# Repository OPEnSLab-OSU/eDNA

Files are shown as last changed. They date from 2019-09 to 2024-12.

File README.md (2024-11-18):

# eDNA Sampler | [Updates](https://github.com/OPEnSLab-OSU/OPEnS-Lab-Home/wiki/eDNA-updates) | [Senior Design Updates](https://github.com/OPEnSLab-OSU/OPEnS-Lab-Home/wiki/eDNA-Senior-Design-Updates) | [Github](https://github.com/OPEnSLab-OSU/eDNA) | [ednaUI](https://github.com/OPEnSLab-OSU/ednaUI) | [ednaServer](https://github.com/OPEnSLab-OSU/ednaServer)

Current Project Team:

Lead: **Marc Belinga** 

Mechanical: **Hendy Kurniawan**

Software:**Marc Belinga** 

Electrical: **Reece Fitch**

## Overview

Organisms leave traces of DNA as they move through their environments. The extraction of these DNA traces is known as environmental DNA (eDNA). eDNA provides scientists and researchers with a non-invasive and sensitive way to detect and quantify species. However, traditional eDNA sampling consists of manually filtering water, which is labor and cost-intensive for remote locations. Furthermore, commercialized solutions are expensive and require a field operator. This eDNA sampler project aims to provide an affordable, open-sourced, remotely deployable, fully automated, and customizable alternative. 

## Description

The eDNA Sampler can run up to 24 inline filter units with support for different conditions including pressure, time, and volume limit. The pumps can deliver a maximum of 350mL/min of flow with each solenoid valve separating the filter housings to minimize cross-contamination. At the end of each sample, the desired stabilizing solution can be injected to fully submerge the filter for long-term storage. An optional river depth sensor can provide a proxy for flow to correct eDNA concentrations to allow for improved quantification of organisms. Data acquired during operation including water depth, pressure, temperature, and flow rate will be stored on a microSD card as a CSV file, which allows easier data export and analysis. A web application is specially designed for the eDNA Sampler for in-field programming, real-time sensor updates, scheduling tasks, and manual operations. The full sampler is estimated to be ~$6000 each.

<p align="center">
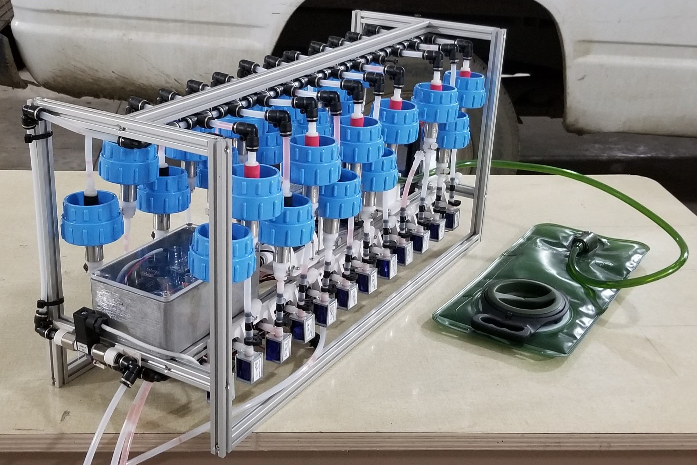
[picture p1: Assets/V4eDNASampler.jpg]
  
</p>

## Field Updates
The eDNA sampler was successfully deployed in Alaska, where it operated under varying levels of turbidity and successfully collected DNA across all conditions. Over the course of six days, the sampler consistently performed three sample collections per day at multiple locations, showcasing its reliability in diverse environments. The battery capacity proved sufficient for multiple days of operation without requiring a recharge, enabling extended fieldwork in remote areas. Additionally, the sampler achieved an average margin of error of 9% in measuring water volume, demonstrating robust performance while highlighting areas for further refinement.

## Objectives

Determining the level of cross-contamination between filters during sampling.
Testing alternatives to ethanol, such as Longmire's solution, for safer and more convenient preservation during field deployments.
Improving the accuracy of water volume measurements using a tipping bucket mechanism.

| Main Control Board     |
|:-------------:|
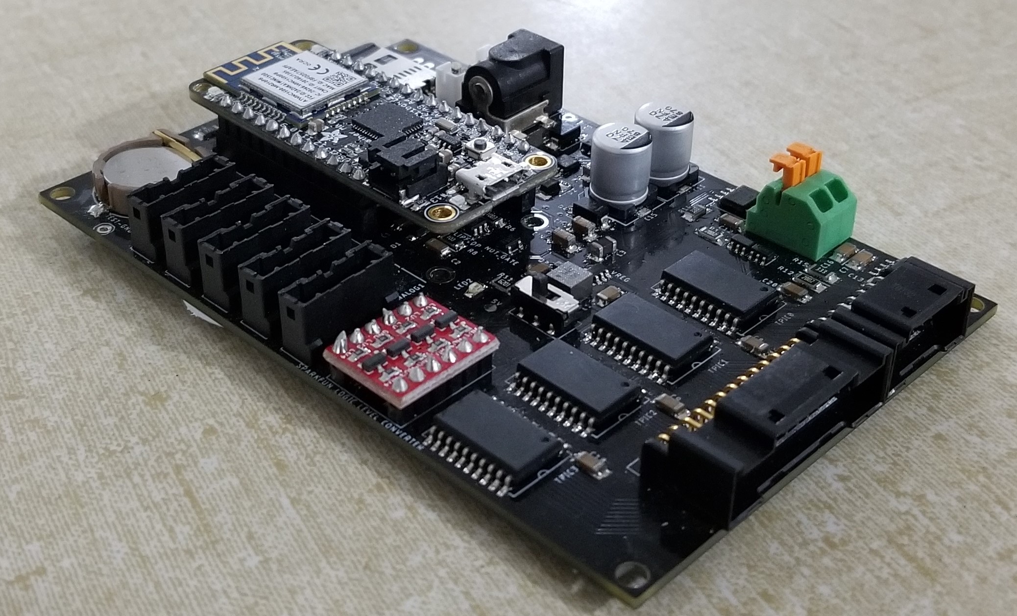
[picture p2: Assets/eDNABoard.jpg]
|      | 

| Browser Application     |
|:-------------:|
|  |

## Future

Finalizing tests for Longmire’s solution to replace ethanol as the preservative.
Implementing a tipping bucket mechanism to improve measurement accuracy.

## Resource List

*  [A Build Guide for the current version (V4) of the eDNA Sampler](https://www.overleaf.com/read/rsvcsjwgfrgj) (Work in Progress)
*  [How to update an assembly in Fusion360](https://www.youtube.com/watch?v=EKoYnxrryUQ)

<!---*  [eDNA GitHub](https://github.com/OPEnSLab-OSU/eDNA)

## [eDNA Updates](https://github.com/OPEnSLab-OSU/OPEnS-Lab-Home/wiki/eDNA-updates) | [Github](https://github.com/OPEnSLab-OSU/eDNA) -->

## Problems & Solutions

Identified logistical challenges with ethanol preservation during field deployment, prompting the exploration of Longmire's solution as an alternative.
While we did average a 9% error in water volume measurements plans are currently being put in place to integrate a tipping bucket to further improve accuracy.
Continued troubleshooting to address filter clogging issues.

Feel free to contact the lab/developer if you have other ideas to solve, improve, or upgrade the eDNA sampler.

Marc Belinga: belingam@oregonstate.edu

## Keywords
eDNA, genomic, sampling, sampler, sample, environmental DNA

## Former Team Members:
Electrical: **Bao Nguyen**, **Sean Booth**,**Jacob Field**, **Kai Roy**

Programming: **Kawin Pechetratanapanit**, **Emannuel Moncada** 

Mechanical: **Torrey Menne**, **Aaron S Arvidson**, **Nikhil Wandhekar**, **Ethan Pohlschneider**, **Tilford Li**, **Danil Kryuchkov**, **Dylan Heisey**, **Joshua Iler**

## Reference
* [Types of Hydraulic Pumps](https://www.youtube.com/watch?v=Qy1iV6EzNHg)

* [eDNA AGU 2019 Poster](https://github.com/OPEnSLab-OSU/OPEnS-Hypnos/files/3996793/eDNA.poster_jsspptx.2.pdf) | [ESSOAR](https://www.essoar.org/doi/abs/10.1002/essoar.10501740.1) | 10.1002/essoar.10501740.1

*  [Inline Pressure Sensor](https://github.com/OPEnSLab-OSU/OPEnS-Lab-Home/wiki/Inline-Pressure-Sensor) (Outdated)

*  [Inline Flow Sensor](https://github.com/OPEnSLab-OSU/OPEnS-Lab-Home/wiki/IDT-Inline-Flow-Sensor) (Outdated)

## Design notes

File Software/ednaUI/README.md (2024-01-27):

# ednaUI 🚀

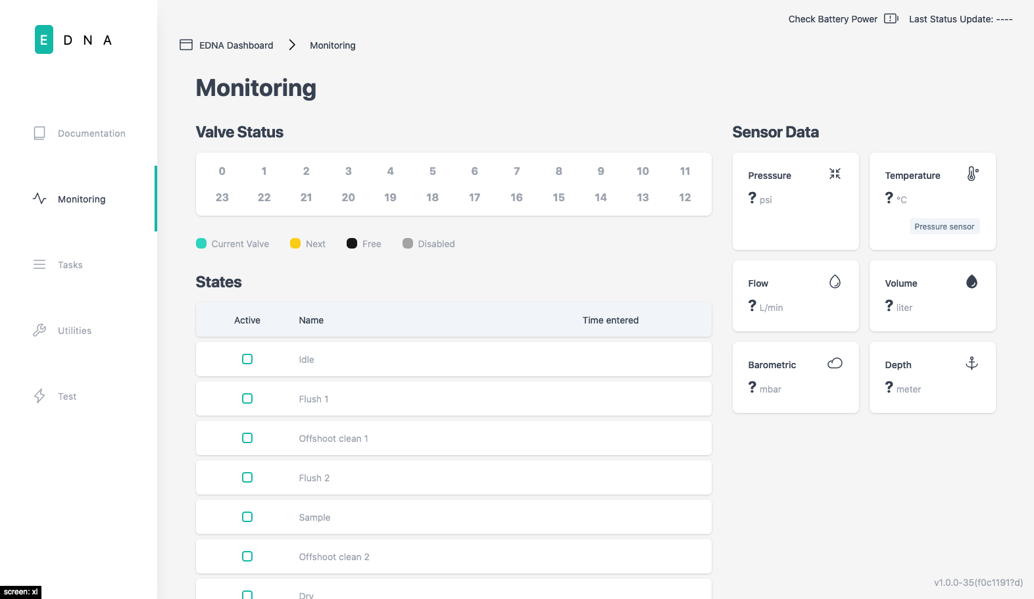
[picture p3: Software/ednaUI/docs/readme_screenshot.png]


### Contributors
- [Kawin Pechetratanapanit](https://github.com/kawinie)
- [Nathan Jesudason](https://github.com/NathanJesudason)

### Top Level Index
- [1 About](#1-about)
- [2 Components](#2-components)
- [3 React Redux Store](#3-react-redux-store)

## 1 About

ednaUI is a browser-based application intended to be used as the primary way for controlling the [ednaServer](https://github.com/OPEnSLab-OSU/eDNA-Server) backend. Uses React, Redux Toolkit, Tailwind CSS, and Webpack.

- Real-time status monitoring of sensor data and states
- Task configuration and management
- Utility functions

## 2 Components
- [2.1 Monitoring](#21-monitoring)
    - [2.1.1 SensorTile](#211-sensortile)
    - [2.1.2 StateTable](#212-statetable)
    - [2.1.3 ValveStatus](#213-valvestatus)
- [2.2 NotFound](#22-notfound)
- [2.3 TaskConfig](#23-taskconfig)
    - [2.3.1 ConfigCard](#231-configcard)
    - [2.3.2 ConfigListItem](#232-configlistitem)
    - [2.3.3 SubmitCard](#233-submitcard)
    - [2.3.4 TaskForm](#234-taskform)
- [2.4 Tasks](#24-tasks)
   - [2.4.1 NewTaskInput](#241-newtaskinput)
   - [2.4.2 TaskTile](#242-tasktile)
- [2.5 Test](#25-test)
- [2.6 Utilities](#26-utilities)

### 2.1 Monitoring
These components are associated with the monitoring tab, giving you information about the current state of the sampler.

#### 2.1.1 SensorTile
The component that holds sensor readings.
#### 2.1.2 StateTable
The component that holds current state information
#### 2.1.3 ValveStatus
The component that keeps track of which valve is available, about to be used, being used, or already used.

### 2.2 NotFound
This is the 404 Page

### 2.3 TaskConfig
These components are associated with the task configuration page, which appear when editting a task.

#### 2.3.1 ConfigCard
This component is used by the TaskForm inside TaskConfig.
#### 2.3.2 ConfigListItem
This component contains a button that takes the user to the top of a page.
#### 2.3.3 SubmitCard
This component handles saving, deleting, scheduling, and unscheduling tasks.
#### 2.3.4 TaskForm
This component holds the values for the various parameters of a task.

### 2.4 Tasks
These components are associated with the tasks tab

#### 2.4.1 NewTaskInput
This component handles entering in a new task name
#### 2.4.2 TaskTile
This component visualizes each of the tasks on the task tab

### 2.5 Test
This is a tab only available in development mode that allows the user to test out a few features.
### 2.6 Utilities
This tab provides all of the utility functions, such as hyperflush and rtc update.

## 3 React Redux Store
- [3.1 Actions](#31-actions)
    - [3.1.1 getStatusUpdate](#311-getstatusupdate)
    - [3.1.2 getTaskCollection](#312-gettaskcollection)
    - [3.1.3 createTask](#313-createtask)
    - [3.1.4 getTask](#314-gettask)
    - [3.1.5 updateTask](#315-updatetask)
    - [3.1.6 deleteTask](#316-deletetask)
    - [3.1.7 scheduleTask](#317-scheduletask)
    - [3.1.8 unscheduleTask](#318-unscheduletask)
    - [3.1.9 setLoadingScreen](#319-setloadingscreen)
- [3.2 models](#32-models)
    - [3.2.1 TaskServerSchema](#321-taskserverschema)
    - [3.2.2 StatusServerSchema](#322-statusserverschema)
- [3.3 reducers](#33-reducers)
    - [3.3.1 status](#331-status)
    - [3.3.2 initialTaskCollection](#332-initialtaskcollection)
    - [3.3.3 taskCollection](#333-taskcollection)
    - [3.3.4 loadingScreen](#334-loadingscreen)

### 3.1 Actions
An action describes what to do with new data after an event.

#### 3.1.1 getStatusUpdate
gets information from the sampler such as valves, currentState, utc, pressure...
#### 3.1.2 getTaskCollection
Gets all tasks from the sampler
#### 3.1.3 createTask
Requests to the sampler to make a new task with a provided name
#### 3.1.4 getTask
Gets a particular task based on its ID
#### 3.1.5 updateTask
Sends updated task information to server
#### 3.1.6 deleteTask
Deletes a task based on its ID
#### 3.1.7 scheduleTask
Schedules a saved task, sending its ID to the sampler
#### 3.1.8 unscheduleTask
Unschedules a task based on its ID
#### 3.1.9 setLoadingScreen
Stores whether the loading screen should be shown or not.

### 3.2 Models
Defines objects to store data in

#### 3.2.1 TaskServerSchema
Defines a task object, and a dictionary of tasks is used to store all tasks
#### 3.2.2 StatusServerSchema
Defines a status object.

### 3.3 Reducers
Reducers take new information and update the state

#### 3.3.1 status
Updates status
#### 3.3.2 initialTaskCollection
Used only in develop, creates an initial list of tasks of random IDs
#### 3.3.3 taskCollection
Updates taskCollection
#### 3.3.4 loadingScreen
Updates whether the loadingScreen should be displayed or not.

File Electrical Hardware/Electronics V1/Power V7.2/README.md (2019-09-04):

# 12V Version 7.2
Power Control Board for microcontroller projects, designed at OPEnS Lab OSU.

The board use a [D-Flipflop](https://www.digikey.com/product-detail/en/texas-instruments/SN74LVC1G175DBVR/296-17617-1-ND/706599) to store the current state of the system.

| D-Flipflop     |
|:-------------:|
|  |

| Schematic Name | Pin Name                  |
|----------------|---------------------------|
| `Q`            | Input - tied HIGH         |
| `D`            | Output to power regulator |
| `CLK`          | Clock                     |
| `!CLR`         | Clear - Reset             |

The flipflop IC is work based on raising, positive edge of the clock (posedge)
The input `D` is always tied HIGH.
The `CLK` is normally pulled low until triggered by the Feather.

> In the original sleep state:
 * `D` is HIGH
 * `Q` is HIGH
 * `CLK` is LOW
 * `CLR` is HIGH

> when the RTC fires the alarm:

`CLR` (reset) is pulled down to GND -> make the output `Q` LOW
		-> Turn on the power regulator. The state remain the same since there is no change in the clock
		
> When Feather fired the shutdown signal:

`CLK` (reset) goes low->high which copy the input `D` to the output `Q`. Since `D` is always high,
		the output `Q` will change to HIGH -> shutdown the voltage regulator

System stay as sleep until the RTC fires again -> reset the flipflop

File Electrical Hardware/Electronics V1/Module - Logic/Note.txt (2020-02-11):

BAO NGUYEN - OPENSLAB

4/24/2019
Disconnect MOSI pin from the board for wifi usesage.
Pin A5, now is connect dirrectly to the main PCB for Shift Register Data
-	A5 --> SHIFTDATA
-	MOSI(M0) is not connected to anything
-	D13 -> HB_IN2 deleted
-	D12 -> HB_IN1 deleted
-	D6 -> HB_IN2 (connect to H-bridge)
-	D5 -> HB_IN1 (connect to H-bridge)

-	D13 -> Button3
-	D12 -> Button2
-	D9  -> Button1

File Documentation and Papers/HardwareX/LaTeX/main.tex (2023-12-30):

% GENERAL INFORMATION: HardwareX is an open access journal established to promote free and open source designing, building and customizing of scientific infrastructure (hardware). For more details on best practices for sharing open hardware see http://www.oshwa.org/sharing-best-practices/

\documentclass[11pt, letterpaper]{article}
\usepackage[utf8]{inputenc}
\usepackage[margin=1.5cm]{geometry} % Default 1.5cm, For review 2cm?
\usepackage{titlesec}
\usepackage{tabu}
\usepackage{enumitem}
\usepackage{amssymb}
\usepackage{xcolor}
\usepackage{verbatim}
\usepackage{graphicx}
\usepackage{setspace}
\usepackage{lineno}
\newlist{selectlist}{itemize}{2}
\setlist[selectlist]{label=$\square$,leftmargin=*,noitemsep,topsep=0pt}

\usepackage{lmodern}

\usepackage{hyperref}
\hypersetup{
    colorlinks=true,
    linkcolor=blue,
    filecolor=magenta,      
    urlcolor=blue,
}
 
\urlstyle{same}

% Set up the section label formatting
\titleformat{\section}[block]{\hspace{1em}\bfseries}{\thesection.}{0.5em}{} 
\titleformat{\subsection}[block]{\hspace{1em}}{\thesubsection}{0.5em}{}

% Settings for Review
%\doublespacing
%\linenumbers

\begin{document}
% Create the title block
\begin{flushleft}

% Remove all text in italics when filling out the template and replace with your manuscripts corresponding text in regular font.
%\textit{Text in italics are template instructions. Remove and replace all instructions with regular font text.}

\setlength{\parindent}{0pt}
\setlength{\parskip}{10pt}
% \textbf{\large HardwareX article template}

%
% Background Information
%
%Insert title
%Max. 20 words. A good title should contain the fewest possible words that adequately describe the content of a paper.
\textbf{Title} \\
PolyWAG: Autonomous filtered water sampling for eDNA 
%\textit{Please avoid acronyms and abbreviations where possible.}

%Insert Authors
\textbf{Authors} \\
Kai Roy * Riley Prince * Marc Belinga * John Selker * Chet Udell
% List all authors. Please mark the corresponding author with (*)

%Insert Affiliations
\textbf{Affiliations} \\ 
(Insert Affiliations)
%\textit{Please include the full address of each author institution}

%Insert Contact Email
%Include institutional email address of the corresponding author
\textbf{Corresponding author’s email address and Twitter handle}\\ 
\textit{Institutional email address preferred. If you have a Twitter handle, please add it here ‘twitter: \@....’}

%Insert Abstract
%Max. 200 words. Remember that the abstract is what readers see first in electronic abstracting and indexing services. This is the advertisement of your article. Make it interesting, and easy to be understood. Be accurate and specific, keep it as brief as possible.
\textbf{Abstract} \\ 
Environmental DNA, eDNA, is an ideal way of researching aquatic environments to determine what species are present in an area the biodiversity of an area, and if any invasive or endangered species are present . Traditional sampling of environmental DNA (eDNA) consists of manually filtering water,  which is labor and cost-intensive for remote locations. Furthermore, commercialized solutions  are either expensive or require a field operator to function.  We have built an eDNA capable of autonomous multi-sampling for a greatly reduced price compared to existing technologies. Our PolyWAG eDNA sampler system is a water sampling device that collects DNA samples via 47mm filter and provides a non-invasive, safe and autonomous means of eDNA collection. The sampler can hold 24 filters and is designed to be easily replaced and reusable. A browser application is used for real-time monitoring, scheduling tasks, and data logging for time, pressure, flow, and filtered volume. Additionally, the sampler design is openly published, modular and is constantly being tested to help us optimize our software and hardware to give us the best results. The 9-step  sampling sequence helps reduce cross contamination significantly. Our machine can be deployed for an extended period. It is completely autonomous and costs around \$6000.

%\textit{Max. 200 words. Remember that the abstract is what readers see first in electronic abstracting \& indexing services - make it brief, specific, interesting and easy to understand. If a research article refers to your hardware, cite that research article here.}

%Insert Keywords
% At least 3 keywords. There is no limit on the no. of keywords you can list. Please remember that effective keywords should not repeat words appearing in your title, and should be neither too general nor too narrow.
\textbf{Keywords}\\
Environmental DNA * Sampling * Arduino * Data Logging \\
%\textit{Add at least 3 keywords and a maximum of 6 keywords.}

%
% Specification Table
%
\newpage
\textbf{Specifications table}\\
% \textit{Please replace the italicizied instructions in the right column of the table with the relevant information about your hardware.}
\vskip 0.2cm
\tabulinesep=1ex
\begin{tabu} to \linewidth {|X|X[3,l]|}
	\hline  
	\textbf{Hardware name} & 
	\textit{PolyWAG}
  	\\
  	\hline 
  	\textbf{Subject area} & 
  	\textit{Environmental, planetary and agricultural sciences}
  	\\
  	\hline 
  	\textbf{Hardware type} & 
  	\textit{Field measurements and sensors}
  	\\ 
	\hline 
	\textbf{Closest commercial analog} &
  	\textit{Dartmouth Ocean Technologies' eDNA Sampler}
  	\\
	\hline \textbf{Open source license} &
  	{CERN Open Hardware License \newline 
  		GNU General Public License v3.0}
  	\\
	\hline \textbf{Cost of hardware} &
  	\textit{\$3800 (Cost of just components)\newline
  		\$6000 (Cost with labor included)}
  	\\
	\hline \textbf{Source file repository} & 
  	% Link to the source file repository
    % insert a DOI URL to an approved source file repository:  Mendeley Data, theOSF, or Zenodo (instructions).  For example: "https://doi.org/10.5281/zenodo.3346799"
    % If there is no external repository write “Available in the article”
  	\textit{If you’ve uploaded your source files to an approved repository (\href{http://osf.io}{\underline{OSF}}, \href{https://data.mendeley.com/}{\underline{Mendeley Data}} or \href{https://zenodo.org/}{\underline{Zenodo}}) write the DOI URL here. For exemple:  \href{http://doi.org/10.17605/OSF.IO/WGK7Q}{http://doi.org/10.17605/OSF.IO/WGK7Q}}  
	% DOI URL to an approved source file repository: \href{https://data.mendeley.com/}{Mendeley Data}, the \href{http://osf.io}{OSF}, or \href{https://zenodo.org/}{Zenodo} \href{https://doi.org/10.5281/zenodo.3346799}{(instructions)}. \linebreak For example: "https://doi.org/10.5281/zenodo.3346799" \linebreak If there is no external repository write “Available in the article"}
  	\\

%\hline \textbf{OSHWA certification UID} \vskip 0.1cm {\it (OPTIONAL)}&
  %Insert OSHWA Certification UID (optional)
%{\it We encourage you to apply for a free \href{https://certification.oshwa.org/}%{\underline{OSHWA Certification}}, which confirms your work is open-source compliant.
%\vskip 0.2cm
%If certification has been acquired, insert the OSHWA UID here. For example: “CH000005”. In your OSHWA certification project description, include a link to your HardwareX publication and the tag \#HX.
%\vskip 0.2cm
%If you haven’t acquired certification, please delete this row of the specifications table.}

\\\hline
\end{tabu}
\end{flushleft}

% create the main body of the paper

\newpage
\section{Hardware in context}

% Include a short description of the hardware, putting into context of similar open hardware and proprietary equipment in the field.
%\textit{Write a short description of the hardware and provide context, i.e., describe similar open hardware and proprietary equipment in the field.}
Environmental DNA (eDNA) is DNA derived from mucus, feces, gametes, and carcasses \cite{web:USGS:eDNA}. Many things can be learned once this DNA is put through sequencing. eDNA can be used to determine what species are present in an area, the biodiversity of an area, and if any invasive or endangered species are present \cite{web:NOAA:eDNA}. eDNA sampling provides scientists and researchers a non-invasive, rapid, cost-effective and sensitive way to detect and quantify species in many environments.  
\newline\par
Traditional sampling of environmental DNA consists of manually filtering water, often requiring one or more researchers to be on location for days or weeks \cite{}. The filtration process varies depending on the researcher, but it is common to pull a sample of water with a bottle and pour that water into a funnel containing a filter. This can be connected to a vacuum pump to expedite the filtering process. After the sampling process is completed, the filters need to be preserved and the setup cleaned to avoid cross contamination \cite{}. This process is labor intensive, cost intensive, and can be dangerous, especially for remote locations. While commercialized solutions to this problem exist, they either still require an operator to be on location or are very expensive. Smithroot’s commercial solution offers a simplified process with additional data collection such as GPS location for a fair price, around \$8,000 \cite{web:smithroot}. A disadvantage of this solution is that it is not fully autonomous, still requiring an operator to be on location to use the device \cite{web:smithroot}. An alternative is the DOT Sampler which is a fully autonomous solution that is capable of multiple samples (20+ samples) and is also submersible but comes at a cost of ~\$55,000 \cite{art:DOT}. 
\newline\par
The solution designed by the OPEnS Lab is the middle ground of these two solutions. While it is not submersible (limiting its potential sampling environments), it is capable of autonomous, multi-sample operations for extended periods of time (approximately one month) for the cost of \$6,000. The two core priorities for our design are its autonomous function and the cross-contamination. The autonomous function of the  sampler is important for a handful of reasons. An autonomous system requires less researcher hours spent in the field. This has cost benefits from the reduced hours worked and safety benefits when sampling in hazardous environments.     

\section{Hardware description}
% Describe the hardware, highlighting the customization rather than the steps of the procedure. Highlight how it differs/which advantage it offers over pre-existing methods. For example, how could this hardware: be compared to other hardware in terms of cost or ease of use, be used in the development of further designs in a particular area, and so on.

% > Add 3-5 bulleted points to broadly explain to other researchers how the hardware could be potentially useful to them, for either standard or novel laboratory tasks, inside or outside of the original user community.

%	\textit{Describe your hardware, highlighting the customization rather than the steps involved in the procedure. Explain how it differs from other hardware and the advantages it offers over pre-existing methods. For example, how does this hardware compare to other hardware in terms of cost or ease of use, or how can it be used to develop further designs in a particular area? 
%	\vskip 0.3cm \noindent
%	Add 3-5 bullet points which broadly explain to other researchers - inside or outside of the original user community - how the hardware could help them, with either standard or novel laboratory tasks.}

The eDNA sampler we have developed is an autonomous multi-sampling device that collects eDNA samples from water via 47mm filter holders and provides a non-invasive, safe, and autonomous means of DNA collection. The sampler can hold 24 of these filter housing and are designed to be easily replaced and reusable. The sampler is controlled by a custom logic board with an Adafruit M0 Feather Wi-Fi microcontroller loaded with a webserver to act as the interface for the sampler’s operations. This webserver hosts a browser application which is used for real-time monitoring, scheduling tasks, and data logging for time, pressure, temperature, flow, and sample volume. This data is located stored onto an SD Card for later data analysis. 

\begin{center}
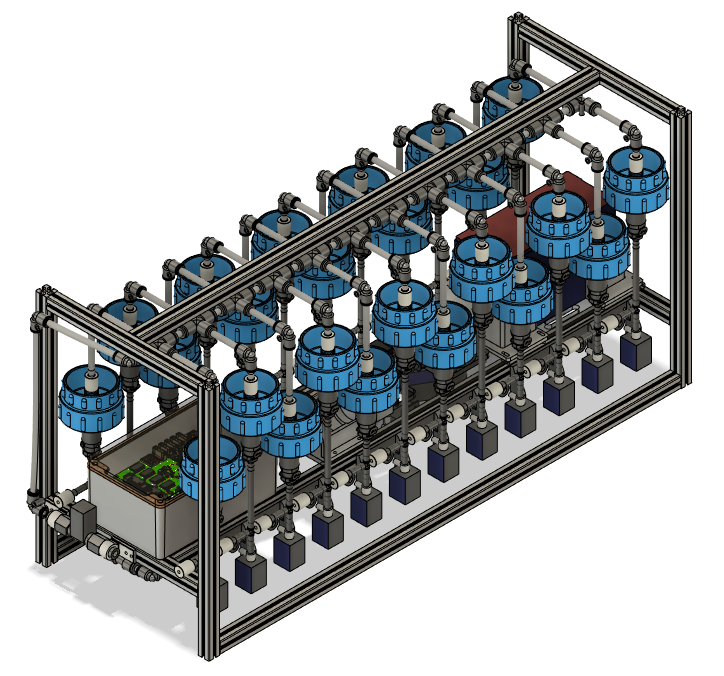
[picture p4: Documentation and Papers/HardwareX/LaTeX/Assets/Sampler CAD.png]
	 %Replace with actualy image?
\end{center}

\subsection{Hydraulics}
The hydraulics of the sampler can be roughly split into the following sections:
\begin{itemize}
	\item The Pump and Inputs
	\item The Lower Hydraulics
	\item The Filters
	\item The Upper Hydraulics and Outputs
\end{itemize}
There are three inputs into the sampler: one for air, one for preservative, and one for water. The preservative input is connected to a hydration bladder where the preservative of choice can be stored. The water input has a prefilter at the front end of the tube to prevent debris from entering the sampler. Three valves are used to control the flow from these inputs with the air preservative being regulated by a solenoid valve and the water being controlled by a ball valve. These three valves connect into a single tube connected to the input of the peristaltic pump.
The pump is capable of 400ml/min of flow under ideal conditions. The output of the pump connects directly into the Lower Hydraulic Rail. 

\begin{center}
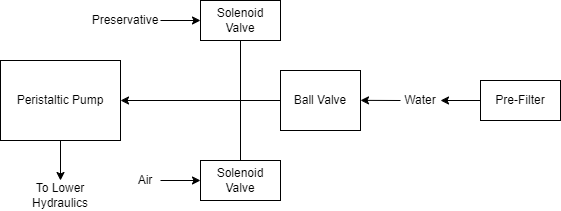
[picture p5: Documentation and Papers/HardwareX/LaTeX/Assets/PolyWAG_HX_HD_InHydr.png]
	
\end{center}

The Lower Hydraulic Rail consists of 24 solenoid valves connected parallel to each other which controls which filter liquid flows through. The valves are split into two sets, one on each side of the sampler. In between these two sets is a M32JM-000105-100PG pressure and temperature sensors. The temperature is logged for later use and the pressure is used for monitoring, stopping an operation if the pressure exceeds a certain margin. At the end of the Lower Hydraulic Rail is another solenoid valve which allows for the lower hydraulics to be purged of their current contents when necessary.

\begin{center}
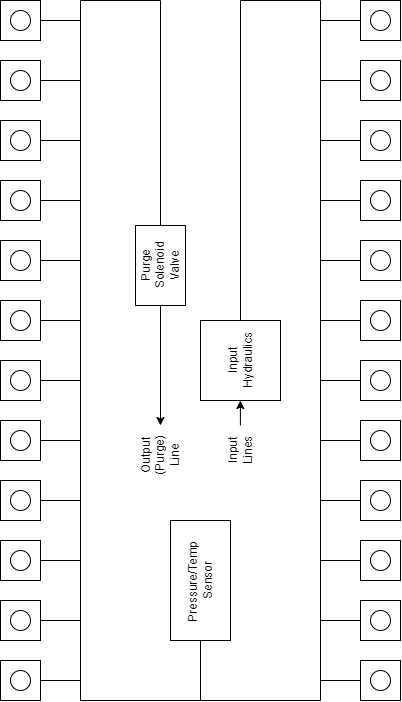
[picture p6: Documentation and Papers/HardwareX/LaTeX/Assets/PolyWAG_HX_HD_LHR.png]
	
\end{center}

After the solenoid valve there is a tee connection that goes to a one-way check valve and a modified Advantec filter. The one-way check valve allows air into the solenoid valve that opens when the pump runs backwards. The Advantec filter is modified with a CPC quick disconnect and a one-way check valve. The one-way check valve is connected to the Upper Hydraulics and is used to prevent liquid from going backwards through the filter. The Upper Hydraulics simply connects the output of all the filters to one central line that goes through a flow meter and out of the sampler. 

\begin{center}
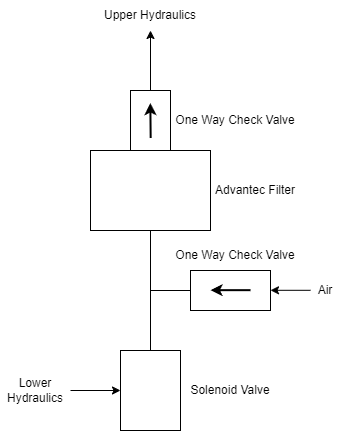
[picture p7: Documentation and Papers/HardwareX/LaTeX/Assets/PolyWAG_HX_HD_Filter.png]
	
\end{center}

\subsection{Sampling Procedure}
Having worked on multiple iterations of the sampler, we have decided to go with a 13-step sampling sequence that helps reduce cross contamination significantly. This sequence can be split into 9 unique steps: Idle, Prefilter Clear, Flush, Offshoot Clean, De-pressure, Sample, Preservative Flush, Preservative, Air Flush, and End.

\begin{center}
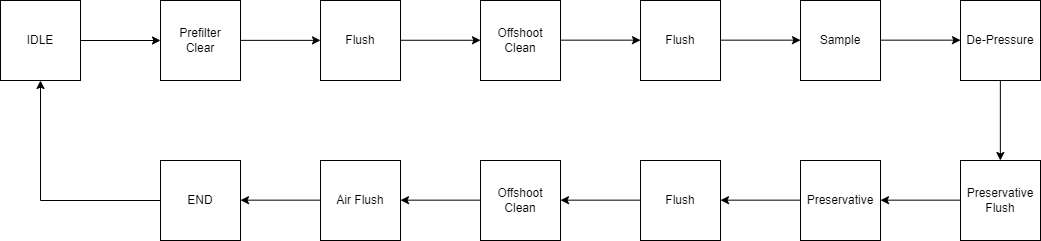
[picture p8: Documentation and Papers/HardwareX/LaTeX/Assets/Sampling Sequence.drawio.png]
	
\end{center}

The Idle state is the default state of the sampler. This is where the sampler waits for a signal from the RTC to move to the first/next state of the Sampling Sequence. If the sampler is not in sleep mode, this is when a client would interact with the UI to do a handful of tasks such as setting up a Sampling Schedule or using the other task utilities. If the sampler is in sleep mode, then only the RTC and supporting circuits are powered. This means there is no way to interact with the sampler without exiting sleep mode.
\newline\par
Once the RTC sends the signal to start a sample procedure, the sampler enters the Prefilter Clear (PC) state. In this state, the purge and input ball valve are opened, and the pump is run in the backwards direction. This will allow for air to flow from the purge and out the input line. This is used to clear the prefilter of anything that might be clogging it, such as accumulated debris. This state runs for X seconds, before moving onto the next state. 
\newline\par
The Flush state and the proceeding Offshoot Clean (OC) state are used to prepare the lower hydraulics before the Sample state. The Flush state starts with the purge valve and the ball valving opening, then the motor starts to run in the forward direction. This fills the lower hydraulics with sample liquid and clears out/dilutes and liquid that remained from previous sample. The Flush state runs for the time specified when the Sampling Schedule is created. We recommend a Flush time of 6 minutes. 
\newline\par
The OC state closes the purge valve and opens the filter valve (for the filter which is about to be used. The pump runs backwards for a few seconds. This clears anything that might be in the tube between the valve and the filter (what we refer to as the offshoot). The Flush state is run one more time before moving to the Sample state.
\newline\par
Like the name suggests, the Sample state is where the system pushes the sample water through the filter. This is done by opening the Filter and Ball Valve and running the pump in the forward direction. The system moves to the next state when the target Sample Volume is reached. This volume is measured by a Flow Meter on the filter output line. Ideally, the state is terminated when the target volume is reached. There is an additional condition that will end the Sample state and that is the Sample Time. This time cutoff was added since the filter clogs and the flow rate decrease rapidly during the sample process. To prevent the sample state running for too long, the time limit was implemented. Both conditions are set during task scheduling. Since the pressure greatly increases due to the clogged filter, the de-pressure state is used to reduce the pressure in the lower hydraulics to ensure that the valves can operate consistently.
\newline\par
The Preservative Flush (PF) and Preservative (P) states are the next states in the sequence after the de-pressure state. The PF state is nearly identical to the Flush state except the Preservative input valve is used instead of the ball valve. The goal of this state is to saturate the lower hydraulics with preservative, preventing additional sample water that may have been stored in the lower hydraulics from going through the filter. If this water was allowed through the filter, then the Sample Volume would be inaccurate by the end of the sequence. The P state is like the Sample state except preservative is the input fluid instead of sample water. This state runs for a time specified by the user during scheduling.  
\newline\par
After the P state, another Flush and OC state runs to purge the leftover preservative in the lower hydraulics. After these two states, an Air Flush (AF) state is run which is identical to the Flush and PF states but uses the air valve as the input instead of the other two inputs. This ensures that any liquid that is in the lower hydraulics is purged. 
\newline\par
After the AF state occurs, the system sets an RTC alarm for the time of the next sample. The system then moves into Idle and if the system was in sleep mode, then the system will go into its low power state.

\subsection{Utilities}

\begin{center}
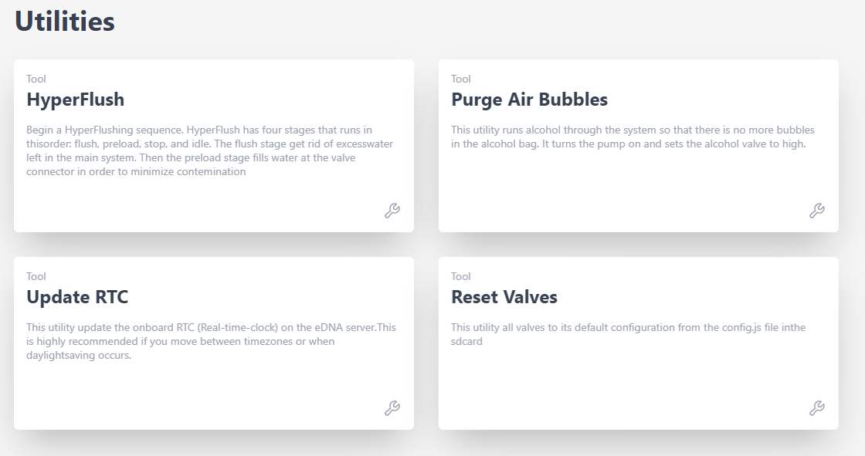
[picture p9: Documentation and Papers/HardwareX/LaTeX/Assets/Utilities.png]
	
\end{center}

The HyperFlush utility runs water through every filter sequentially for a few seconds per filter. This is mainly used for cleaning out the system after a sample task (i.e., a set of 24 samples) to prevent any unwanted cross contamination. This utility can also be used to test the basic functionality of the sampler, as nearly every component is activated during this sequence. 
\newline\par
The Preservative Air Purge (PAP) utility turns the pump on and opens the alcohol valve for 10 seconds. This runs some alcohol through the system and removes air bubbles from the alcohol bag. Often it helps to use this utility multiple times and to tilt the Preservative Bladder so that the air is near the port.
\newline\par
The Update RTC utility is needed to make sure that the time on the sampler matches your local time, so scheduling a task will remain accurate. Whenever the system is fully depowered (ie the battery is removed), or when new code is uploaded to the microcontroller, the RTC will need to be updated. It is also recommended that the RTC is updated when there is a daylight-saving change, or when you move between time zones.
\newline\par
The Reset Valves Utility is used when valves have been sampled that you want to be sampled again. This is required since the system ‘locks’ the filter valves when they have been used in a sample, this prevents samples from being corrupted accidentally. The code does not let you sample a valve multiple times without being reset to prevent messing up a sample. It is important to note that this utility will reset all valves, not a specific one.

\subsection{Electronics}
\begin{center}
	
\end{center}

The PolyWAG Sampler is designed with a custom electronics control board that can be split into 8-10 blocks with an Adafruit Feather M0 at its core. These blocks consist of the microcontroller/Wifi Block, Power, RTC, and sleep control blocks, and the output blocks consisting of the Shift Register, Pump, and Ball-Valve H-Bridge Blocks. 

\begin{center}
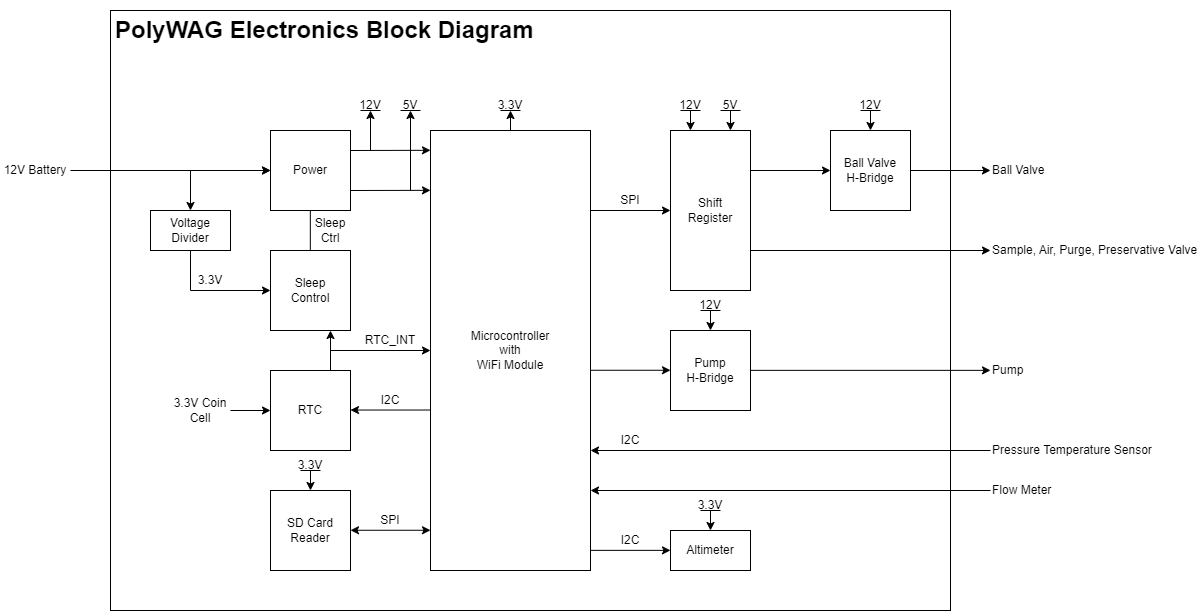
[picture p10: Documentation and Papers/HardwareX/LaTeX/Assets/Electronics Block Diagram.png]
	
\end{center}

The power block consists of a reverse polarity current (RPC) circuit and a voltage regulator circuit. The RPC Circuit was added to protect the 12V battery from current flowing backwards through the system. While the battery has its own protection circuits, they lock the battery in the case of a short and need to be reset using the battery charger. The RPC circuit was added to prevent any “permanent” power loss while in the field. The voltage regulator circuit is a 12V to 5V regulator with an enable pin that connects to the sleep control circuit. This is used to save power during long term deployments. 
\newline\par
The RTC and sleep control circuit are used to keep track of time and to save power respectively. The sleep control circuit controls the output of the power circuit and is constantly being power by a simple voltage divider circuit. It is basically a Flip Flop circuit that is reset when the RTC triggers an interrupt. The RTC circuit is used to keep track of the time between samples and is powered by a coin cell while power is off. This allows it to keep accurate track of time and signals an interrupt when its internal alarm is triggered. This interrupt is used to both turn power back on and to inform the microcontroller that it is time for a sample. If noise causes the sleep control circuit to reactivate power, the microcontroller will see that the RTC did not trigger the interrupt and will fall back into power saving mode. 
\newline\par
The shift register circuit consists of 4 8-bit shift registers connect to the microcontroller via SPI. The shift registers are pull-down style shift registers where the ‘output’ pins are pulled to ground. This allows the shift registers to control devices that use higher logic voltages. This allows us to control the 27 12V solenoid valves with a 5V IC. The shift registers are also used to control the H-bridge for the Ball valve. The H-bridge for the pump is controlled directly by the microcontroller itself. 
\newline\par
The board contains an SD Card circuit for datalogging purposes. The data is logged every second and includes the current state, time, and data from the sensors. The sensors include an in-line pressure temperature sensors for monitoring the lower hydraulic line and a flow meter out the output for measuring volume.
\newline\par
The microcontroller of choice is an Adafruit Feather M0 WiFi. The WiFi version of the Feather M0 was chosen as the user interface requires the feather to host a webserver. 

\subsection{User Interface}

\begin{center}
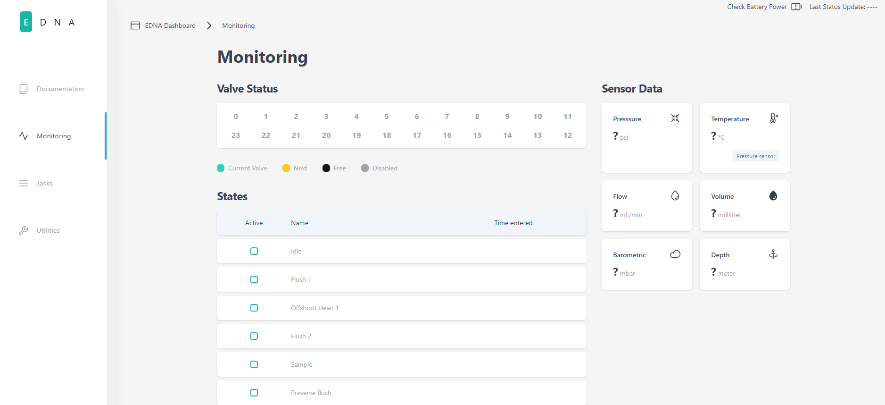
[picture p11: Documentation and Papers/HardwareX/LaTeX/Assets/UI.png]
	
\end{center}

PolyWAG Sampler hosts a webserver that can be connected to via a browser. This acts as the user interface for the system. There are three main sections that make up the user interface: monitoring, tasks, and utilities. The monitoring page displays the data from the sensors, the current state of the sampling procedure, and information on the sampling valves such as the current valve being sampled, and which valves are locked and unlocked. The utilities page is used to activate the utilities mentioned earlier. The tasks page is where sampling tasks are created. Multiple tasks can be created, and each task is saved in memory for later modification and use. This page is also where tasks can be scheduled for sampling. Each task contains the information on which valves are being used as well as for how long each state occurs. 

\subsection{Task Configuration}

\section*{\textit{Design files}}
% The  complete  design  files  must  be  either  uploaded  to  an  approved  online  repository,  uploaded  at the  time  of  submission  on  the  online  Editorial  Manager  submission  interface  as  supplementary materials [CAD files, videos,. . . ], or included in the body of the manuscript [e.g.  figures].  The three approved  online  repositories  are  Mendeley  Data,  the  Open  Science  Framework,  and  Zenodo. See repository instructions: https://doi.org/10.5281/zenodo.3346799

% Design files should be in preferred format for making modifications. See OSHWA’s open-source definition for details: https://www.oshwa.org/definition/

\textit{Your design files should be editable - see \href{https://www.oshwa.org/definition/}{OSHWA’s open source definition of ‘Documentation’} for further details. You must then either:}
\begin{itemize}
\item[$\bullet$]{\it Upload your design files to one of the three approved online repositories - \href{https://data.mendeley.com/}{Mendeley Data} (\href{https://doi.org/10.5281/zenodo.3346799}{instructions}), the \href{https://osf.io/}{Open Science Framework} (\href{https://osf.io/wgk7q/wiki/home/}{instructions}) or \href{https://zenodo.org/}{Zenodo} (\href{https://doi.org/10.5281/zenodo.3346799}{instructions}). We recommend this option as the repositories support versioning of files.}
\item[$\bullet$]{\it Upload your design files as supplementary materials (e.g., CAD files, videos…) to Hardware X’s online editorial system when you submit your manuscript.}
\item[$\bullet$]{\it Include your design files in the body of the manuscript (e.g., as figures).}
\end{itemize}

%
%\textit{The complete design files must be either uploaded to an approved online repository, uploaded at the time of submission on the online \href{https://editorialmanager.com/ohx/}{Editorial Manager} submission interface as supplementary materials [CAD files, videos,\dots], or included in the body of the manuscript [e.g. figures]. The three approved online repositories are \href{https://data.mendeley.com/}{Mendeley Data}, the \href{http://osf.io}{Open Science Framework}, and \href{https://zenodo.org/}{Zenodo}. See repository instructions \href{https://doi.org/10.5281/zenodo.3346799}{here}. Design files should be in preferred format for making modifications. See \href{https://www.oshwa.org/definition/}{OSHWA’s open-source definition} for details.}
%\begin{itemize}
\vskip 0.1 cm
\noindent
\textit{\underline{CAD files:} You are encouraged to use free and open source software packages for creating the files. For CAD files, \href{http://www.openscad.org/}{OpenSCAD}, \href{http://www.freecadweb.org/}{FreeCAD}, or \href{https://www.blender.org/}{Blender} are encouraged, but, if these are not available, we accept source files from proprietary CAD packages, such as Autocad or Solidworks, and other drawing packages.} 
\vskip 0.1 cm
\noindent
\textit{\underline{3D printing:} Supplementary files that facilitate digital replication of the devices are encouraged;  for example, STL files for 3D printing components. We recommend uploading CAD files to the \href{http://3dprint.nih.gov/}{\underline{NIH 3D Print Exchange}} as Custom Labware and then entering the link here.} 
\vskip 0.1 cm
\noindent
\textit{\underline{Electronics:} PCB layouts and other electronics design files can be uploaded to the \href{http://www.ohwr.org/}{\underline{Open Hardware Repository}} or other repositories or as supplementary materials.} 
\vskip 0.1 cm
\noindent
\textit{\underline{Software and firmware:} All software files used in the design and operation of the hardware should be included in the repository. Provide a description of the software and firmware and use extensive comments in the code.}

\section{Design files summary}
\textit{Complete a separate row for each design file associated with your hardware (including the primary design files). Any empty rows should be deleted.}
% Please include a summary of all design files for your hardware by filling rows of the table below
\vskip 0.1cm
\tabulinesep=1ex
\begin{tabu} to \linewidth {|X|X|X[1.5,1]|X[1.5,1]|} 
\hline
\textbf{Design filename} & \textbf{File type} & \textbf{Open source license} & \textbf{Location of the file} \\\hline
%Insert design files
\textit{For example: Design file 1} & \textit{e.g. CAD file, figures, videos} & \textit{All designs must be submitted under an open hardware license. Enter the corresponding open source license for the file.} & \textit{Either enter the URL for the repository or the sentence: "Available with the article".}  \\\hline
\dots & \dots & \dots & \dots \\\hline
\dots & \dots & \dots & \dots \\\hline
% Design file 3 & File type & License & Link \\\hline
\end{tabu}

% For each design file listed in the summary above, include a short description of the file below (one or two sentences)
\vskip 0.3cm
\noindent
\textit{For each design file listed in the summary table above, include a short description of the file below (just one or two sentences per design file).}

\section*{\textit{Bill of materials}}
% For a complex Bill of Materials, the complete Bill of Materials (editable spreadsheet file e.g., ODS file type or PDF file) can be uploaded in an open access online location such as the Open Science Framework repository. Include the link here. Alternatively, the Bill of Materials can be uploaded at the time of submission on the online Elsevier submission interface as supplementary material.

% > To make it easy to tell which item in the Bill of Materials corresponds to which component in your design file(s), use matching designators in both places, or otherwise explain the correspondence.

% > For material type, select from: Metal, semi-conductor, ceramic, polymer, biomaterial, organic, inorganic, composite, nanomaterial, semiconductor, non-specific, or other 

% > \href{https://osf.io/}{\underline{Open Science Framework}} 
Given the number of materials required to build a PolyWAG Sampler, The BOM will be located in an external file and can be found \href{https://docs.google.com/spreadsheets/d/1WZbGYL1k3ne1a8Z1YOA0necr3MgxMj_BiEK7JuaGnzE/edit#gid=1118434588}{\underline{here}}
% Change the link for one that points to Zenodo
% > Add the BOM to Zenodo

\section{Build instructions}
%Provide detailed, step by step instructions for the construction of the reported hardware include all necessary information for reproducing the submitted hardware.
% > Explain and, when possible, characterize design decisions. Including design alternatives if they exist. 
% > Use visual instructions such as schematics, images, and videos. 
% > Clearly reference design files and component parts described in the Design File Summary and Bill of Materials. 
% > Highlight potential safety concerns that may arise

Given the complexity of the PolyWAG Sampler, a Build Instructions section of sufficient detail would be near a hundred pages long. This is why an external build guide document will be linked for those who are interested in knowing how one of these samplers are assembled. This file can be located \href{https://drive.google.com/file/d/1QSpYj-N6-jE-VbXLVelzRzzdIF1lMkuC/view?usp=sharing}{\underline{here}}
% Change the link for one that points to Zenodo
% > Add the Build Guide to Zenodo

\section{Operation instructions}
%Provide detailed instructions for the safe and proper operation of the hardware. 
%> Step-by-step operational instructions for operating the hardware. 
%> Use visual instructions as necessary. 
%> Highlight potential safety hazards.

%%% Kai's Notes
%%% Use Mark's section here
%%% Maybe add a section for physically using the sampler. 

\section{Validation and characterization}
%Demonstrate the operation of the hardware and characterize its performance over relevant critical metrics
%> Demonstrate the use of the hardware for a relevant use case. 
%> If possible, characterize performance of the hardware over operational parameters. 
%> Create a bulleted list that describes the capabilities (and limitations) of the hardware. For example consider descriptions of load, operation time, spin speed, coefficient of variation, accuracy, precision and etc. 

%%% Kai's Notes
%%% Insert Riley's Section once edits are made. 

\section*{}
\noindent
\textbf{Ethics statements}\\

\noindent
The work does not use any human or animal subjects.\\

\noindent
\textbf{CRediT author statement}\\
% CRediT is in initiative that enables authors to share an accurate and detailed description of their diverse contributions to a published work.
% Example:
% Zhang San: Conceptualization, Methodology, Software. Priya Singh: Data curation, Writing- Original draft preparation. Wang Wu: Visualization, Investigation. Jan Jansen: Supervision. Ajay Kumar: Software, Validation. Sun Qi: Writing- Reviewing and Editing.
% Please add a CRediT author statement for your data article here, using the \href{https://www.elsevier.com/authors/journal-authors/policies-and-ethics/credit-author-statement}{categories listed on this webpage}.

\noindent
\textbf{Kai Roy}: Project administration, Hardware(Electrical), Validation, Writing- Original draft \\
\noindent
\textbf{Riley Prince}: Project administration, Methodology, Validation, Data curation, Writing- Original draft \\
\noindent
\textbf{Marc Belinga}: Software, Investigation, Writing- Original draft \\
\noindent
\textbf{Torrey Menne}: Conceptualization, Hardware\\
\noindent
\textbf{Bao Nguyen}: Project administration, Conceptualization, Hardware(Electrical)\\
\noindent
\textbf{Nikhil Wandhekar}: Project administration, Hardware\\
\noindent
\textbf{Nathan Jesudason}: Software, Validation \\
\noindent
\textbf{Kawin Pechetratanapanit}: Conceptualization, Software \\
\noindent
\textbf{John Selker}: Funding acquisition, Supervision \\
\noindent
\textbf{Chet Udell}: Funding acquisition, Supervision \\
\noindent
\textbf{Cara Walter}: Funding acquisition, Supervision, Resources \\

\noindent
\textbf{Auther}: Contribution. \\

\noindent
\textbf{Acknowledgements}\\
% [List here those individuals who provided help during the research (e.g., providing language help, writing assistance or proof reading the article, etc.).] Please also identify who provided financial support for the conduct of the research and/or preparation of the article and to briefly describe the role of the sponsor(s), if any, in study design; in the collection, analysis and interpretation of data; in the writing of the report; and in the decision to submit the article for publication. If the funding source(s) had no such involvement then this should be stated.}

\noindent
\textit{All contributors who do not meet the criteria for authorship should be listed in an acknowledgments section.} 
\vskip 0.2cm
\noindent
\textit{In addition, please list any funding sources in this section. List funding sources in this standard way to facilitate compliance to funder's requirements:}
\vskip 0.2cm
\noindent
\textit{Funding: This work was supported by the National Institutes of Health [grant numbers xxxx, yyyy]; the Bill \& Melinda Gates Foundation, Seattle, WA [grant number zzzz]; and the United States Institutes of Peace [grant number aaaa].}
\vskip 0.2cm
\noindent
\textit{It is not necessary to include detailed descriptions on the program or type of grants and awards. When funding is from a block grant or other resources available to a university, college, or other research institution, submit the name of the institute or organization that provided the funding.}
\vskip 0.2cm
\noindent
\textit{If no funding has been provided for the research, please include the following sentence:}
\vskip 0.2cm
\noindent
\textit{This research did not receive any specific grant from funding agencies in the public, commercial, or not-for-profit sectors.
}\\

%
% References
%
%> Include at least one reference, to the original publication of the hardware you customized.
%> Include other references as required. Include references to put your device in context in the literature. For more information on the reference format in HardwareX please see the Guide for Authors at: https://www.elsevier.com/journals/hardwarex/2468-0672/guide-for-authors
\bibliography{refs}
\bibliographystyle{IEEEtran}

\end{document}

%> Author manuscript checklist
%> ●	HardwareX is a journal dedicated to the exhaustive and fully open source communication of advances in scientific infrastructure. Upon submission the author declares that all information necessary to reproduce the subject of the submission (e.g. bill of materials, build instructions, calibration procedures, source files, code, and safety considerations) is communicated in full and is accessible for use under an open source license. 
%> ●	Is the subject of the submission under an open source license? Are design files in the preferred format for making modifications? As defined by the Open Source Hardware definition. 
%> ●	Can the hardware be reproduced with the details provided in the submission?
%> ●	Are all relevant design files available on Mendeley Data, the Open Science Framework, or Zenodo repositories, described in the Summary of Design Files document, and clearly documented? (e.g. descriptive file names, commented code, labeled images, etc.) 
%>      ○	If in the Open Science Framework, the repository has be registered? Instructions
%>      ○	If in Zenodo, the repository is open access and is published? Instructions
%>      ○	If in Mendeley Data, the repository is published or the sharable link was included in the additional information of the Editorial Submission interface? Instructions
%> ●	Are visual instructions used when necessary?
%> ●	Is the utility of the hardware to the scientific community? Has a specific scientific application been demonstrated using the hardware?
%> ●	Is the performance of the hardware adequately demonstrated and characterized?
%> ●	Are all potential safety concerns addressed?
%> ●	For more information on the article template consult the Guide to Authors.}

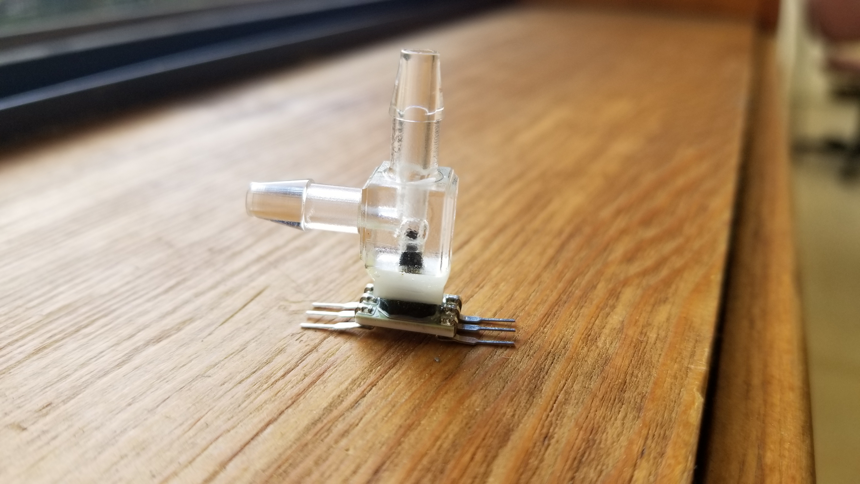
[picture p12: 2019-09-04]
Electrical Hardware/Electronics V1/Sensor - Inline Pressure/Images/Inline1.jpg

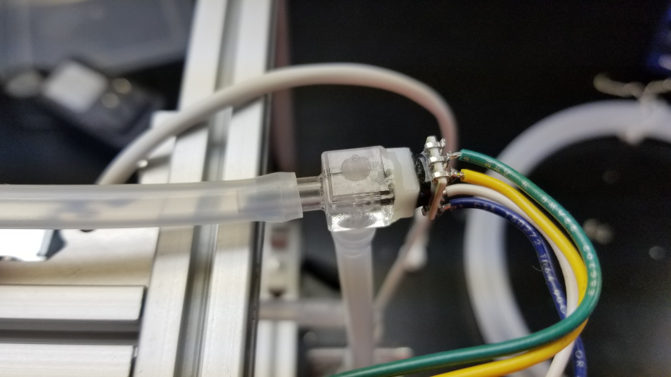
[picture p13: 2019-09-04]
Electrical Hardware/Electronics V1/Sensor - Inline Pressure/Images/Inline2.jpg

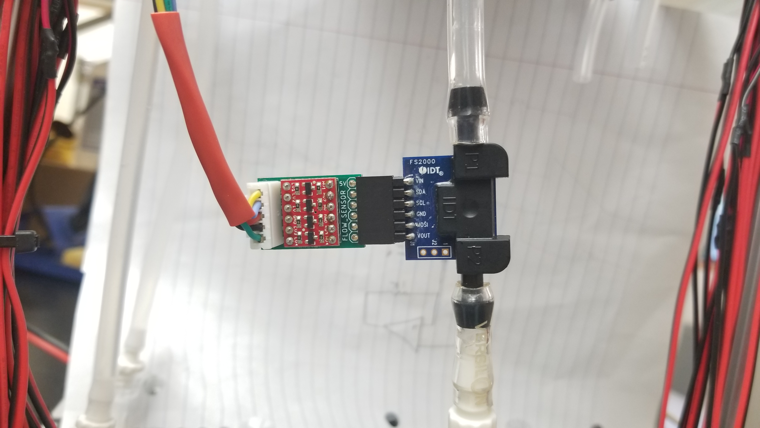
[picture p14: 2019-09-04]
Electrical Hardware/Electronics V1/Sensor - Flow/FlowSensor.jpg

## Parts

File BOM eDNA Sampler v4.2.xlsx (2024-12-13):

Part Name | 0 | Description | Units | Part Number | Price/Pack | Pack Size | Total Price (Per Unit) | Total Price (Per Pack)
Electrical
PolyWAG Main Control Board | GoogleDrive (https://docs.google.com/spreadsheets/d/1zhdDUbpBKhYvQ1EmbM6KhN0UHYbMQTIm4_g4Q-LcJn0/edit) | Main PCB for eDNA Sampler | 1 |  | $139.38 | 1 | $139.38 | $158.92
12V Battery (10Ah) | Dakota Lithium | Battery for eDNA 10Ah | 1 |  | $99.00 | 1 | $99.00 | $99.00
Battery charger (12V, 3A) | Dakota Lithium (https://dakotalithium.com/product/dakota-lithium-12v-battery-charger/) | Battery charger w/ Alligator Clips | 1 |  | $29.00 | 1 | $29.00 | $29.00
Battery Connector | Amazon (https://www.amazon.com/MUYI-Waterproof-Connector-1-5mm-Terminal/dp/B01A6LTK44) | (Pack of 5) Waterproof Connector for Battery | 1 |  | $5.99 | 1 | $5.99 | $5.99
Wiring - 6 Color | Amazon (https://www.amazon.com/LotFancy-Stranded-Electrical-Flexible-insulated/dp/B07Q3G1VG2/) | 22AWG PVC Wiring Kit 6 colors | 1 |  | $16.00 | 1 | $16.00 | $16.00
Solder Seal Connector (White) | Amazon (https://www.amazon.com/Connectors-Haisstronica-Electrical-Waterproof-White26-24/dp/B07J3V7SB3) | 100PC Solder Seal White | 1 |  | $11.99 | 1 | $11.99 | $11.99
Solder Seal Connector (Blue) | Amazon | 50PC Solder Seal Blue | 4 |  | $10.99 | 50 | $0.88 | $10.99
Solder Seal Connector (Red) | Amazon | 50PC Solder Seal Red | 2 |  | $9.99 | 50 | $0.40 | $9.99
Electronics Box Assembly
Electronics Box | Polycase | Metal Electronics Box | 1 | AN-17P-01 | $33.58 | 1 | $33.58 | $33.58
25mm PCB Spacers | Amazon | 25mm PCB Spacers | 4 | Black 25mm M3 Spacer | $11.49 | 10 | $4.60 | $11.49
M4 Self Threading Screws | McMaster-Carr | 10mm M4 Thread Forming Screws | 4 | 94209A678 | $10.56 | 25 | $1.69 | $10.56
Wiring Cable Gland | Amazon (https://www.amazon.com/Lokman-Plastic-Waterproof-Adjustable-Connectors/dp/B06Y5HGYK2?pldnSite=1) | PG9 Cable Gland | 4 |  | $9.99 | 20 | $2.00 | $9.99
Sensors
Flow Meter | Amazon (https://www.amazon.com/CIXIFM-Meters-Liquid-Hydraulic-Industrial/dp/B09DCJGPCD) | Cixi M5.2-AL Flow Meter | 1 |  | $350.00 | 1 | $350.00 | $350.00
Flow Meter Tube Fitting | McMaster (https://www.mcmaster.com/7610N115/) | 1/4"OD to 1/8 Pipe Fitting | 2 | 7610N115 | $12.12 | 1 | $24.24 | $24.24
Pressure Sensor | Digikey (https://www.digikey.com/en/products/detail/te-connectivity-measurement-specialties/M32JM-000105-100PG/9695477) | M32JM-000105-100PG Pressure Sensor | 1 | 223-1893-ND | $96.98 | 1 | $96.98 | $96.98
Pressure Sensor Fitting | McMasterCarr (https://www.mcmaster.com/5779K131/) | 1/4" NPT Female to 1/4" Air Push-to-connect | 1
3-Pin Waterproof Connector | Amazon (https://www.amazon.com/Waterproof-Extension-Cable%EF%BC%8CWaterproof-Connector-Connector%EF%BC%8Cled/dp/B0989V4VXD) | Waterproof Connector for 3-Pin Sensors | 1 |  | $9.99 | 6 | $1.67 | $9.99
4-Pin Waterproof Connector | Amazon (https://www.amazon.com/Waterproof-Connector-connector%EF%BC%8Crgb-Cable%EF%BC%8Cled-waterproof/dp/B07KK9J6VC) | Waterproof Connector for I2C Sensors | 1 |  | $9.99 | 6 | $1.67 | $9.99
Hydraulic
Pump Components
Peristaltic Pump | Amazon (https://www.amazon.com/Self-Priming-Peristaltic-Aquarium-Chemicals-Additives/dp/B07J2JDT54) | 12 V Peristaltic pump | 1 |  | $44.20 | 1 | $44.20 | $44.20
Pump - Capacitor | Digikey (https://www.digikey.com/en/products/detail/kemet/C322C104K1R5TA/818104) | Capacitor 100nF DIP 50V | 4 | 399-4328-ND | $0.82 | 1 | $3.28 | $3.28
Pump Tubing | McMaster (https://www.mcmaster.com/5229K58/) | 1/4" ID 3/8" OD Durometer (25ft Pump Tubing) | 1 | 5229K58 | $23.25 | 1 | $23.25 | $23.25
Vulcanizing Tape | Grainger (https://www.grainger.com/product/ER-TAPE-Self-Fusing-Tape-3DXU8) | Self-Fusing Tape, Silicone Rubber 1in x 36ft | 1 | 3DXU8 | $2.00 | 1 | $2.00 | $2.00
Hose Clamps | McMasterCarr | 35.5mm 316 SS Hose Clamp | 1 | 5011T261 | $24.20 | 20 | $1.21 | $24.20
Pre-Filter Components
Pre-Filter Screen | Grainger (https://www.grainger.com/product/GRAINGER-APPROVED-3-3-4-in-Polypropylene-Filter-6UJJ7) | 3.75" Polypropylene Filter Screen | 1 | 6UJJ7 | $11.70 | 1 | $11.70 | $11.70
Tubing Gland | Amazon (https://www.amazon.com/Lokman-Plastic-Waterproof-Adjustable-Connectors/dp/B06Y5HGYK2?pldnSite=1) | PG7 Cable Gland | 1 |  | $8.99 | 20 | $0.45 | $8.99
120mm M6 Bolt | McMaster-Carr | M6x120mm 316SS Bolts | 2 | 92290A793 | 4.03 | 1 | $8.06 | $8.06
M6 Nylock Nut | McMasterCarr | M6 Locknut (316 SS) | 2 | 94205A153 | $3.75 | 10 | $0.75 | $3.75
Filter Housing Components
Spring Check Valve | McMasterCarr (https://www.mcmaster.com/7757k42) | Spring Check Valve 1psi | 24 | 7757k42 | $4.11 | 1 | $98.64 | $98.64
Advantec Filter Housing | VWR | Advantec 47mm Filter Holder | 24 | 43303020 | $46.05 | 1 | $1105.20 | $1105.20
CPC Socket PMC w/ Shutoff | CPC (https://products.cpcworldwide.com/en_US/ProductsCat/IVD/PMC1/PMCD1004?tracking=searchterm:PMCD1004) | Quick-Connect Socket 1/4NPT WITH SHUTOFF | 24 | PMCD1004 | $7.05 | 1 | $169.20 | $169.20
1/4" NPT Coupling | BFO (https://www.buyfittingsonline.com/pipe-fittings-stainless-steel-1-4-in-full-coupling-316-ss-threaded-npt-32-n/) | 1/4" NPT 316 SS Coupling | 24 | 32-N | $3.08 | 1 | $73.92 | $73.92
Heat Shrink Double Walled Tubing | Amazon (https://www.amazon.com/Pack-inch-Heat-Shrink-Tubing/dp/B07LD9DCWH) | 3/4" Heat Shrink | 1 | 2pack x 4ft | $10.49 | 1 | $10.49 | $10.49
Teflon Tape | Grainger (https://www.grainger.com/product/ANTI-SEIZE-TECHNOLOGY-Thread-Sealant-Tape-4X543?opr=APPD&analytics=altItems_5X584) | 1/2" Teflon Tape | 1 | 4X543 | $3.00 | 1 | $3.00 | $3.00
Filter Mounting
Spring Check Valve | McMasterCarr (https://www.mcmaster.com/7757k42) | Spring loaded check valve 1 PSI | 24 | 7757k42 | $4.11 | 1 | $98.64 | $98.64
3/16" Barbed Tee | Reptile Basics (https://www.reptilebasics.com/3-16-t-fitting) | 3/16" Barbed Tee Fitting | 24 |  | $22.50 | 50 | $10.80 | $22.50
CPC Plug PMC w/out Shutoff | CPC (https://products.cpcworldwide.com/en_US/ProductsCat/IVD/PMC1/PMC2203?tracking=searchterm:PMC2203) | Quick-Connect Plug 3/16 Barb NO SHUTOFF | 24 | PMC2203 | $1.07 | 1 | $25.68 | $25.68
Solenoid Valve | From Factory (http://www.dyxminipump.com/en/show-93-73-1.html) | Shenzhen Solenoid Valve | 27 | DSF2-A | $2.70 | 1 | $72.90 | $72.90
Plastic Ball Valve w/ SS Gears | Aliexpress (https://www.aliexpress.com/item/1005001279231940.html) | 1/2'' PVC Motorized Ball Valve DC12V + Indicator only + 12V + NPT + CR201 + Fastship | 1 |  | $31.58 | 1 | $31.58 | $31.58
Ball Valve Push-to-connect | Amazon (https://www.amazon.com/Malida-Connect-Fitting-Reverse-Osmosis/dp/B01M3Q42CX) | 1/4" NPT Male to 1/4" Air Push-to-connect | 2 |  | $0.90 | 10 | $0.18 | $0.90
Tubing (Thin Walled) | McMasterCarr (https://www.mcmaster.com/5181k39) | 1/4 OD PE tubing 50ft - Thin Walled | 1 | 5181K39 | $5.50 | 1 | $5.50 | $5.50
Tubing (Thick Walled) | McMasterCarr (https://www.mcmaster.com/5181K24/) | 1/4 OD 1/8 ID PE tubing 25ft - Thick Walled for Pressure | 1 | 5181K24 | $3.25 | 1 | $3.25 | $3.25
4-Way Cross Connector | Amazon (https://www.amazon.com/MacCan-Pneumatic-Union-Connect-Fittings/dp/B07ZN7GGHL?s=industrial) | Push-to-connect Cross 1/4 OD | 11 |  | $15.00 | 10 | $16.50 | $30.00
3-Way Tee Connector | Amazon (https://www.amazon.com/Tailonz-Pneumatic-Plastic-Connect-Fittings/dp/B07PFQ91VY) | Push-to-connect Tee 1/4 OD | 28 |  | $13.00 | 10 | $36.40 | $39.00
2-Way Corner Connector | Amazon | Push-to-connect Elbow 1/4 OD | 38 |  | $8.99 | 10 | $34.16 | $35.96
Union Straight connector | Amazon (https://www.amazon.com/dp/B07STMGW9M) | Push-to-connect Straight 1/4 OD | 4 |  | $11.00 | 10 | $4.40 | $11.00
Push Connect Plugs | Amazon (https://www.amazon.com/Tailonz-Pneumatic-Push-Connect-Fitting/dp/B07STVD3RR?s=industrial) | 1/4" Push-to-connect Plugs | 26 |  | $9.99 | 20 | $12.99 | $19.98
Barb Reducer | McMasterCarr (https://www.mcmaster.com/5463K152-2974K263/) | Bard reducer 1/4ID to 3/16ID | 2 | 5463K152 | $1.03 | 10 | $0.21 | $1.03
Alcohol Reservoir | Amazon (https://www.amazon.com/Hydration-Reservoir-Military-Replacement-Climbing/dp/B071DQSZB8) | 2 Liter Hydration Bladder with Quick Disconnect | 1 |  | $15.99 | 1 | $15.99 | $15.99
Frame
Aluminum Extrusion 610mm | Misumi (https://us.misumi-ec.com/vona2/detail/110300465870/?Inch=0&CategorySpec=00000042747::15) | Aluminum Extrusion 610mm | 5 |  | $3.47 | 1 | $17.35 | $17.35
Aluminum Extrusion 310mm | Misumi (https://us.misumi-ec.com/vona2/detail/110300465870/?Inch=0&CategorySpec=00000042747::15) | Aluminum Extrusion 310mm | 4 |  | $1.76 | 1 | $7.04 | $7.04
Aluminum Extrusion 200mm | Misumi (https://us.misumi-ec.com/vona2/detail/110300465870/?Inch=0&CategorySpec=00000042747::15) | Aluminum Extrusion 200mm | 4 |  | $2.64 | 1 | $10.56 | $10.56
Aluminum Extrusion 80mm | Misumi (https://us.misumi-ec.com/vona2/detail/110300465870/?Inch=0&CategorySpec=00000042747::15) | Aluminum Extrusion 80mm | 1 |  | $2.64 | 1 | $2.64 | $2.64
Center Component Acrylic Sheet | McMasterCarr (https://www.mcmaster.com/8560K215/) | 3/16" Clear Acrylic Sheet | 0.2 | 8560K215 | $47.09 | 1 | $9.42 | $47.09
Fasteners
27mm M3 Bolt | Fastner Express (https://www.fastener-express.com/M3x.5x27mmSocketHeadCapScrewsPlainAluminumQty.aspx) | M3 x .5 x 27mm Socket Head Cap Screws 7075 T6 Plain Aluminum | 2 | ASHM3027-7P4 | $28.36 | 50 | $28.36 | $28.36
18mm M3 Bolt | McMasterCarr (https://www.mcmaster.com/92290A761/) | 18mm M3 Socket Machine Screws (316 SS) | 2 | 92290A761 | $14.18 | 1 | $28.36 | $28.36
16mm M3 Bolt (LP) | McMasterCarr (https://www.mcmaster.com/90666A107/) | 16mm M3 Socket Machine Screw (LP) 316 SS | 1 | 90666A107 | $15.18 | 1 | $15.18 | $15.18
12mm M3 Bolt (LP) | McMasterCarr (https://www.mcmaster.com/90666A106) | 12mm M3 Socket Machine Screws (LP) (316 SS) | 3 | 90666A106 | $12.44 | 1 | $37.32 | $37.32
8mm M3 Bolt (LP) | McMasterCarr | 8mm M3 Socket Machine Screws (LP) (316 SS) | 1 | 90666A104 | $11.52 | 1 | $11.52 | $11.52
M3 Square Nut | McMasterCarr (https://www.mcmaster.com/97258A101/) | M3 Square Nuts (304 SS) | 4 | 97258A101 | $10.00 | 1 | $40.00 | $40.00
M3 Washer | McMasterCarr (https://www.mcmaster.com/95211a120) | M3 Washer 9mm OD (316 SS) | 2 | 95211A120 | $4.76 | 1 | $9.52 | $9.52
M3 Nylock Nut | Grainger (https://www.grainger.com/product/FABORY-M3-0-50-Nylon-Insert-Lock-6CB80) | M3 Locknut (316 SS) | 1 |  | $5.24 | 1 | $5.24 | $5.24
M4 Nylon Hex Nut | Amazon (https://www.amazon.com/100PCS-Nylon-Replacement-Plastic-Nuts/dp/B07LFW8ZSM) | Used as a Spacer | 4 |  | $6.99 | 100 | $0.28 | $6.99
Heat insert | Amazon (https://www.amazon.com/iplusmile-Embedment-Threaded-Printing-Projects/dp/B087NBYF65) | Heat insert M3 | 4 |  | $13.89 | 100 | $0.56 | $13.89
3D Printed Components | OPEnS Lab | Filament Quantity in Grams: | 240 |  | $0.25 | 1 | $60.00 | $60.00
Assembly
80 Qt Pelican Cooler | Pelican (https://www.pelican.com/us/en/product/coolers/wheeled-cooler/elite/80qt?sku=80QW-2-TAN) | Sampler Housing | 1 |  | $514.95 | 1 | $514.95 | $514.95
Conformal Coating | Amazon (https://www.amazon.com/MG-Chemicals-Silicone-Conformal-Coating/dp/B085G42TGS) | Silicone conformal coating | 1 |  | $12.95 | 1 | $12.95 | $12.95
Electrical Tape | Amazon (https://www.amazon.com/Scotch-Heat-Resistant-Listed-Certified-Electrical/dp/B001AXD0EY) | Scotch Electrical Tape | 1 |  | $1.99 | 1 | $1.99 | $1.99
Cable Sleeve | Amazon (https://www.amazon.com/XHF2018-Spiral-Organizer-Polyethylene-6MM-Length15M/dp/B07JPJ6QBV) | 12mm cable sleeve coil | 1 |  | $7.99 | 1 | $7.99 | $7.99
 |  |  |  |  |  | Price: | $3536.44 | $3753.07
 |  | Labor Cost Estimation | Hours | Rate per Hour | Totals
 |  | Electrical | 25 | $16.00 | $400.00 |  | $2000.00 | $2000.00
 |  | Frame | 40 |  | $640.00
 |  | Hydraulic | 40 |  | $640.00
 |  | Testing and Debugging | 20 |  | $320.00
 |  | Supervision and programming | 10 | $40.00 | $400.00 |  | $400.00 | $400.00
 |  | Total Person Hours: | 125
 |  |  |  |  |  | Shipping | $179.65 | $179.65
 |  |  |  |  |  | Price: | $6116.09 | $6332.72
Maintenance
Silicone Tubing for pump | McMaster (https://www.mcmaster.com/5229K58/) | 1/4" ID 3/8" OD Durometer (25ft Pump Tubing) | 1 | 5229K58 | $23.25 |  |  | $10.70
MCE Gridded Membrane Filter | Amazon (https://www.amazon.com/Membrane-Solutions-Lab-Supply-Diameter/dp/B075XJ96RJ) | Diameter 47 mm, Pore Size: 0.45 um, pack of 100 | 1 | MFMCE047045GWS | $22.99 |  |  | $22.99
Tools for Assembly
Soft tube cutter | Amazon (https://www.amazon.com/RIDGID-23488-PC-1250-Single-Plastic/dp/B0019MLSLS) | Single Stroke Plastic Pipe and Tubing Cutter | 1 |  | $16.99 |  |  | $16.99
2mm Hex driver | McMaster Carr | 2mm Hex Screw Driver | 1 | 7440A78 | $7.05 |  |  | $7.05
2.5mm Hex Driver | McMasterCarr (https://www.mcmaster.com/52975A16/) | 2.5mm Hex Screw Driver | 1
Wrench M3 nut | Amazon (https://www.amazon.com/uxcell-Metric-Double-Wrench-5-5mm/dp/B07D4B8GWW) | 5.5mm Socket (M3 Nut) | 1 |  | $5.49 |  |  | $5.49
Frame Drill Bit | McMasterCarr (https://www.mcmaster.com/29305A13/) | 1/8" Drill Bit | 2 | 29305A13 | $5.23
Countersink Bit | McMasterCarr (https://www.mcmaster.com/2910A13/) | 1/8" Bit Countersink Attachment | 1 | 2910A13 | $17.20
M3 Through Hole Tap | McMasterCarr (https://www.mcmaster.com/2673A71/) | M3 Tap | 1 | 2673A71 | $17.93 |  |  | $17.93
Alternate Parts
Ball Valve Push to Connects | McMasterCarr (https://www.mcmaster.com/7610N116/)

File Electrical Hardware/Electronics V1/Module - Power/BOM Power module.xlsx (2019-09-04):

Name | Part Number | Amount | Footprint | Link | Unit Price | Price | Note
Sparkfun logic level shifter | 1568-1209-ND | 1 | DIP12 | Digikey (https://www.digikey.com/products/en?mpart=BOB-12009&v=1568) | 2.95 | 2.95
12 pins angle female header | S5448-ND | 1 | Through hole | Digikey (https://www.digikey.com/product-detail/en/sullins-connector-solutions/PPTC121LGBN-RC/S5448-ND/775906) | 0.80 | 0.80
Capacitor 100nF DIP 50V | 399-4328-ND | 10 | Through hole | Digikey (https://www.digikey.com/product-detail/en/kemet/C322C104K1R5TA/399-4328-ND/818104) | 0.29 | 2.92 | C1 C2 C3 C4 C5 C6 C8 C10 C13 C14
Resistor 64K ohm 3.5mm | PPC60.4KXCT-ND | 2 | Through hole | Digikey (https://www.digikey.com/product-detail/en/vishay-bc-components/SFR16S0006042FR500/PPC60.4KXCT-ND/594861) | 0.20 | 0.40
Capacitor 470uF SMD 16V | 493-2181-1-ND | 4 | SMD | Digikey (https://www.digikey.com/product-detail/en/nichicon/UWT1C471MNL1GS/493-2181-1-ND/590156) | 0.51 | 0.51 | C7 C15 C16
Motor Connector - Push in | 277-12184-ND | 1 | DIP2 | Digikey (https://www.digikey.com/product-detail/en/phoenix-contact/1864286/277-12184-ND/6605434) | 0.96 | 0.96
NOT gate - Inverter | TC4S584FLFCT-ND | 2 | SOT753 - SC74A | Digikey (https://www.digikey.com/product-detail/en/toshiba-semiconductor-and-storage/TC4S584FLF/TC4S584FLFCT-ND/870444) | 0.44 | 0.88 | Low power
Capacitor 100nF SMD | 1276-1017-1-ND | 2 | 1206 | Digikey (https://www.digikey.com/product-detail/en/samsung-electro-mechanics/CL31B104KBCNNNC/1276-1017-1-ND/3889103) | 0.12 | 0.24 | C11, C12
JST angle Connector | 455-2257-ND | 24 | 2.5mm DIP | Digikey (https://www.digikey.com/product-detail/en/jst-sales-america-inc/S2B-XH-A-LF-SN/455-2257-ND/1651055) | 0.16 | 3.86
JST regular connector | 455-2247-ND | 6 | 2.5 mm DIP | Digikey (https://www.digikey.com/products/en?keywords=455-2247-ND) | 0.15 | 0.90
Flyback Diode for valves | 1N4148W-FDICT-ND | 33 | SOD123 | Digikey (https://www.digikey.com/product-detail/en/diodes-incorporated/1N4148W-7-F/1N4148W-FDICT-ND/815280) | 0.15 | 4.98 | 3 extra added
Capacitor 150pF 50V | BC1043CT-ND | 2 | Through hole | Digikey (https://www.digikey.com/product-detail/en/vishay-bc-components/K151J15C0GF5TH5/BC1043CT-ND/286665) | 0.25 | 0.50 | C17, C18
Resistor 20K ohm | CR1206-FX-2002ELFCT-ND | 2 | 1206 | Digikey (https://www.digikey.com/product-detail/en/bourns-inc/CR1206-FX-2002ELF/CR1206-FX-2002ELFCT-ND/3767632) | 0.10 | 0.20
TPIC6B596 | 296-1351-1-ND | 4 | 20-SOIC | Digikey (https://www.digikey.com/product-detail/en/texas-instruments/TPIC6B595DWR/296-1351-1-ND/404964) | 1.42 | 5.68
DRV8871DDAR H Bridge | 296-43024-1-ND | 2 | 8-SOIC | Digikey (https://www.digikey.com/product-detail/en/texas-instruments/DRV8871DDAR/296-43024-1-ND/5722182) | 2.17 | 4.34
 |  |  |  | Total without PCB |  | 30.13
PCB | 25.32 |  |  | Total with PCB |  | 55.44
Ferrite Bead |  | 1 | Ring | Digikey (https://www.digikey.com/product-detail/en/laird-signal-integrity-products/28B0375-100/240-2067-ND/255586) | 0.3 | 0.3 | Just for NOTE

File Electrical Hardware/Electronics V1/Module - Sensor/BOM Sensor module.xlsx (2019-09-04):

Name | Part Number | Amount | Extra | Footprint | Link | Unit Price | Price | Price w extra | Note
2.5mm audio jack - 4 conductors | CP-SJ-2504A-SMT-DKR-ND | 5 | 0 | SMD | Digikey (https://www.digikey.com/product-detail/en/cui-inc/SJ-2504A-SMT-TR/CP-SJ-2504A-SMT-DKR-ND/6619427) | 1.14 | 5.70 | 5.7
30k ohm resistor 5% | P30KECT-ND | 6 | 2 | 1206 | Digikey (https://www.digikey.com/product-detail/en/panasonic-electronic-components/ERJ-8GEYJ303V/P30KECT-ND/203313) | 0.10 | 0.60 | 0.8
10k ohm resistor | A130183CT-ND | 2 | 1 | 1206 | Digikey (https://www.digikey.com/product-detail/en/te-connectivity-passive-product/CRGCQ1206J10K/A130183CT-ND/8578015) | 0.10 | 0.20 | 0.3
10k ohm resistor | CF14JT10K0CT-ND | 2 | 1 | through hole | Digikey (https://www.digikey.com/product-detail/en/stackpole-electronics-inc/CF14JT10K0/CF14JT10K0CT-ND/1830374) | 0.10 | 0.20 | 0.3 | Pull up resistor for I2C
2x4 header male | 609-3362-ND | 5 | 0 | through hole | Digikey (https://www.digikey.com/product-detail/en/amphenol-icc-fci/68602-108HLF/609-3362-ND/1878479) | 0.48 | 2.40 | 2.4
1x6 angle female header | S5481-ND | 1 | 1 | through hole | Digikey (https://www.digikey.com/product-detail/en/sullins-connector-solutions/PPPC061LGBN-RC/S5481-ND/775939) | 0.66 | 0.66 | 1.32
1x6 angle male header | S1111EC-40-ND | 1 |  | through hole | Digikey (https://www.digikey.com/product-detail/en/sullins-connector-solutions/PRPC040SBAN-M71RC/S1111EC-40-ND/2775294) | 0.83 | 0.83 | 0.83
JST 2.5mm 5pos | 455-2270-ND | 1 |  | through hole | Digikey (https://www.digikey.com/product-detail/en/jst-sales-america-inc/B5B-XH-A-LF-SN/455-2270-ND/1530483) | 0.25 | 0.25 | 0.25
Pressure Sensor MS5803-02BA | 223-1624-5-ND | 1 |  | 8-SMD | Digikey (https://www.digikey.com/product-detail/en/te-connectivity-measurement-specialties/MS580302BA01-00/223-1624-5-ND/5277629) | 10.72 | 10.72 | 10.72
Capacitor 0.1uF | 311-1488-1-ND | 1 | 1 | 1206 | Digikey (https://www.digikey.com/product-detail/en/yageo/CC1206KKX7R0BB104/311-1488-1-ND/2833794) | 0.19 | 0.19 | 0.38
PCB |  |  |  |  |  | 21.70 | 7.23
 |  |  |  |  | Total without PCB |  | 21.75 | 23
 |  |  |  |  | Total with PCB |  | 28.98 | 30.23

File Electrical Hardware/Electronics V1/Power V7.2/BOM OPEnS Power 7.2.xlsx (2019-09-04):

Source | Component | Qty | Component ID | Unit Price | Total | Board ID
Digikey (https://www.digikey.com/product-detail/en/texas-instruments/LM2575SX-5.0-NOPB/LM2575SX-5.0-NOPBCT-ND/3440104) | Switching Regulator | 1 | LM2575Sx-5.0/NOPBCT-ND | 3.04 | 3.04
Digikey (https://www.digikey.com/product-detail/en/cui-inc/PJ-002AH-SMT-TR/CP-002AHPJCT-ND/669692) | Barrel Jack | 1 | CP-002AHPJCT-ND | 1.44 | 1.44 | 12V_IN
Digikey (https://www.digikey.com/product-detail/en/panasonic-electronic-components/EEE-1AA101WR/PCE3867CT-ND/766243) | Capacitor 100 uF 16V | 1 | P15086CT-ND | 0.32 | 0.32 | C12
Digikey (https://www.digikey.com/product-detail/en/nichicon/UWT1C471MNL1GS/493-2181-1-ND/590156) | Capacitor 470 uF 16V | 1 | 493-2181-1-ND | 0.51 | 0.51 | C13
Digikey (https://www.digikey.com/product-detail/en/yageo/CC1206KKX7R0BB104/311-1488-1-ND/2833794) | Capacitor 0.1 uF | 4 | 311-1488-1-ND | 0.19 | 0.76 | C1, C2, C3, C4
Digikey (https://www.digikey.com/product-detail/en/wurth-electronics-inc/744770247/732-1690-1-ND/1994270) | Inductor 470 uH | 1 | 732-1690-1-ND | 2.25 | 2.25 | L1
Digikey (https://www.digikey.com/product-detail/en/yageo/RC1206FR-0710KL/311-10.0KFRCT-ND/731430) | Resistor 10k 1% | 2 | 311-10.0KFRCT-ND | 0.1 | 0.2 | R3, R4, R5
Digikey (https://www.digikey.com/product-detail/en/yageo/RC1206FR-07130KL/311-130KFRCT-ND/731485) | Resistor 130k 1% | 1 | 311-130KFRCT-ND | 0.1 | 0.1 | R1
Digikey (https://www.digikey.com/product-detail/en/yageo/RC1206FR-07300KL/311-300KFRCT-ND/731752) | Resistor 300k 1% | 1 | 311-300KFRCT-ND | 0.1 | 0.1 | R2
Digikey (https://www.digikey.com/product-detail/en/stackpole-electronics-inc/RNCP1206FTD1K50/RNCP1206FTD1K50CT-ND/2240679) | Resistor 1.5k 1% | 1 | RNCP1206FTD1K50CT-ND | 0.1 | 0.1 | R6
Digikey (https://www.digikey.com/product-detail/en/diodes-incorporated/S1A-13-F/S1A-FDICT-ND/750031) | Diode General SMD | 2 | S1A-FDICT-ND | 0.24 | 0.48 | D2, D4
Digikey (https://www.digikey.com/product-detail/en/texas-instruments/SN74LVC1G175DBVR/296-17617-1-ND/706599) | D Flip Flop SOT23-6 | 1 | 296-17617-1-ND | 0.37 | 0.37
Digikey (https://www.digikey.com/product-detail/en/micro-commercial-co/2N7002-TP/2N7002-TPMSCT-ND/1960099) | MOSFET N-Type | 1 | 2N7002-TPMSCT-ND | 0.18 | 0.18 | Q1
Digikey (https://www.digikey.com/product-detail/en/vishay-semiconductor-diodes-division/BZD27C4V3P-E3-08/BZD27C4V3P-E3-08GICT-ND/6680647) | Diode - Zener 5.1V | 1 | BZD27C4V3P-E3-08GICT-ND | 0.41 | 0.41 | D1
Digikey (https://www.digikey.com/product-detail/en/keystone-electronics/3000TR/36-3000CT-ND/1532229) | Battery Holder 12mm | 1 | 36-3000CT-ND | 0.91 | 0.91
Digikey (https://www.digikey.com/products/en?keywords=DS3231SN%23T%26RCT-ND) | DS3231 RTC | 1 | DS3231SN#T&RCT-ND | 8.77 | 8.77
OSHPARK | PCB |  |  |  | 3.48
 |  |  |  | Total | 23.42

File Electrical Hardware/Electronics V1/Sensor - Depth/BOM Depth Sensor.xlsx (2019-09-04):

Name | Part Number | Amount | Footprint | Link | Unit Price | Bulk Price | Price
SparkFun Differential I2C Breakout - PCA9615 | BOB-14589 | 2 | Board | Sparkfun (https://www.sparkfun.com/products/14589) | 10.95 |  | 21.9
Pressure Sensor MS5803-02BA | 223-1624-5-ND | 1 | 8-SMD | Digikey (https://www.digikey.com/product-detail/en/te-connectivity-measurement-specialties/MS580302BA01-00/223-1624-5-ND/5277629) | 10.72 | 10.72 | 10.72
1-1/2" PVC pipe - 4 inches |  | 1 |  | HomeDepot
1-1/2" PVC pipe cap | 294217 | 2 |  | HomeDepot (https://www.homedepot.com/p/Charlotte-Pipe-1-1-2-in-PVC-Sch-40-Socket-Cap-PVC021161400HD/203811676) | 1.14 |  | 2.28
Ethernet Cable Cat5e - Outdoor 66ft |  | 1 |  | Amazon (https://www.amazon.com/Cable-External-Outdoors-Internal-Networking/dp/B016S76U0C?s=gateway) | 21.99 |  | 21.99
Strain relieve protector |  | 1 |  | Amazon | 0.66 | 6.55 | 0.66
Capacitor 0.1uF SMD |  | 1 | 1206 | Digikey
PCB for pressure sensor |  | 1 |  | OSHPark | 0.58 |  | 0.58
 |  |  |  | Total |  |  | 58.13

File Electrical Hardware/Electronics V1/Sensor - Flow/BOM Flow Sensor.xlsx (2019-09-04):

Name | Part Number | Amount | Footprint | Link | Unit Price | Price | Note
JST Connector 5pos Female 2.5mm | 455-2270-ND | 2 | Through hole | Digikey (https://www.digikey.com/product-detail/en/jst-sales-america-inc/B5B-XH-A-LF-SN/455-2270-ND/1530483) | 0.25 | 0.5
JST Connector 5pos Male 2.5mm | 455-2268-ND | 2 | Through hole | Digikey (https://www.digikey.com/product-detail/en/jst-sales-america-inc/XHP-5/455-2268-ND/1125486) | 0.12 | 0.24
IDT Flow sensor up to 1L/min - Calibrated | FS2012-1002-LQ | 1 | Through hole | Mouser (https://www.mouser.com/ProductDetail/IDT/FS2012-1002-LQ) | 78.28 | 78.28 | 7.79 shipping
Logic Level Converter | 1568-1209-ND | 1 | Through hole | Digikey (https://www.digikey.com/product-detail/en/sparkfun-electronics/BOB-12009/1568-1209-ND/5673795&) | 2.95 | 2.95
6 POS female header 2.54mm | S7039-ND | 1 | Through hole | Digikey (https://www.digikey.com/product-detail/en/sullins-connector-solutions/PPPC061LFBN-RC/S7039-ND/810178) | 0.53 | 0.53
 |  |  |  | Total without PCB |  | 82.5

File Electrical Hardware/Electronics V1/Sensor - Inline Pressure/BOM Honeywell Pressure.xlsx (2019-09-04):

Name | Part Number | Amount | Footprint | Link | Unit Price | Bulk Price | Price
JST Connector 4pos Female 2.5mm | 455-2249-ND | 1 | through hole | Digikey (https://www.digikey.com/product-detail/en/jst-sales-america-inc/B4B-XH-A-LF-SN/455-2249-ND/1651047) | 0.21 | 0.21 | 0.21
JST Connector 4pos Male 2.5mm | 455-2267-ND | 1 |  | Digikey (https://www.digikey.com/product-detail/en/jst-sales-america-inc/XHP-4/455-2267-ND/683353) | 0.10 | 0.10 | 0.10
Honeywell Pressure Sensor ABPDANT030PG0D3 | 785-ABPDANT030PG0D3 | 1 | through hole | Mouser (https://www.mouser.com/ProductDetail/Honeywell/ABPDANT030PG0D3) | 15.06 | 15.06 | 15.06
Capacitor 0.1uF SMD | 311-1488-1-ND | 1 | 1206 | Digikey (https://www.digikey.com/product-detail/en/yageo/CC1206KKX7R0BB104/311-1488-1-ND/2833794) | 0.19 | 0.19 | 0.19
PCB |  |  |  |  | 0.58 |  | 0.58
 |  |  |  |  | Total with PCB |  | 16.14

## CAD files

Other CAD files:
Mechanical Hardware/eDNA V4/25mm+M3+Frame+Screws.f3d
Mechanical Hardware/eDNA V4/3D Printable/Air+Purge+Valve+Mount.f3z
Mechanical Hardware/eDNA V4/3D Printable/Ball+Valve+(Marine+Mockup).f3d
Mechanical Hardware/eDNA V4/3D Printable/Ball+Valve+Mount+(Marine).f3d
Mechanical Hardware/eDNA V4/3D Printable/Battery+Mount.f3d
Mechanical Hardware/eDNA V4/3D Printable/Flow+Sensor+Mount.f3d
Mechanical Hardware/eDNA V4/3D Printable/Intake+and+Outflow+Tube+Routing.f3d
Mechanical Hardware/eDNA V4/3D Printable/V4+Solenoid+Hanger.f3d
Mechanical Hardware/eDNA V4/3D Printable/sensorclip.f3d
Mechanical Hardware/eDNA V4/7688N111_Vented+Plastic+Submersible+Cord+Grip.f3d
Mechanical Hardware/eDNA V4/Acrylic+CNC+Case+Top.f3d
Mechanical Hardware/eDNA V4/Alcohol+valve+mount.f3z
Mechanical Hardware/eDNA V4/AlumCase.f3z
Mechanical Hardware/eDNA V4/Aluminum+Case+Top.f3d
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

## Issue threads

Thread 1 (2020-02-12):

### ISSUE TITLE
RTC INT pulling to ground but not triggering

### ISSUE THREAD

**Issue by StephenMoreOSU** [OPEnSLab-OSU/eDNA#1]
Tested using rtc trigger from Kawin, the code was functioning properly, however, RTC_Read was reading 1.44V from voltage divider across pullup and 30k resistor. The M0 was not reading the trigger.

FIX:
The solution to the bug was to take out the 30k between RTC_INT and RTC_Read and short the circuit, this allowed for the M0 to read trigger when RTC_INT was pulled down.

**Comment by kawinie** [comment]
Wrote RTC code for testing

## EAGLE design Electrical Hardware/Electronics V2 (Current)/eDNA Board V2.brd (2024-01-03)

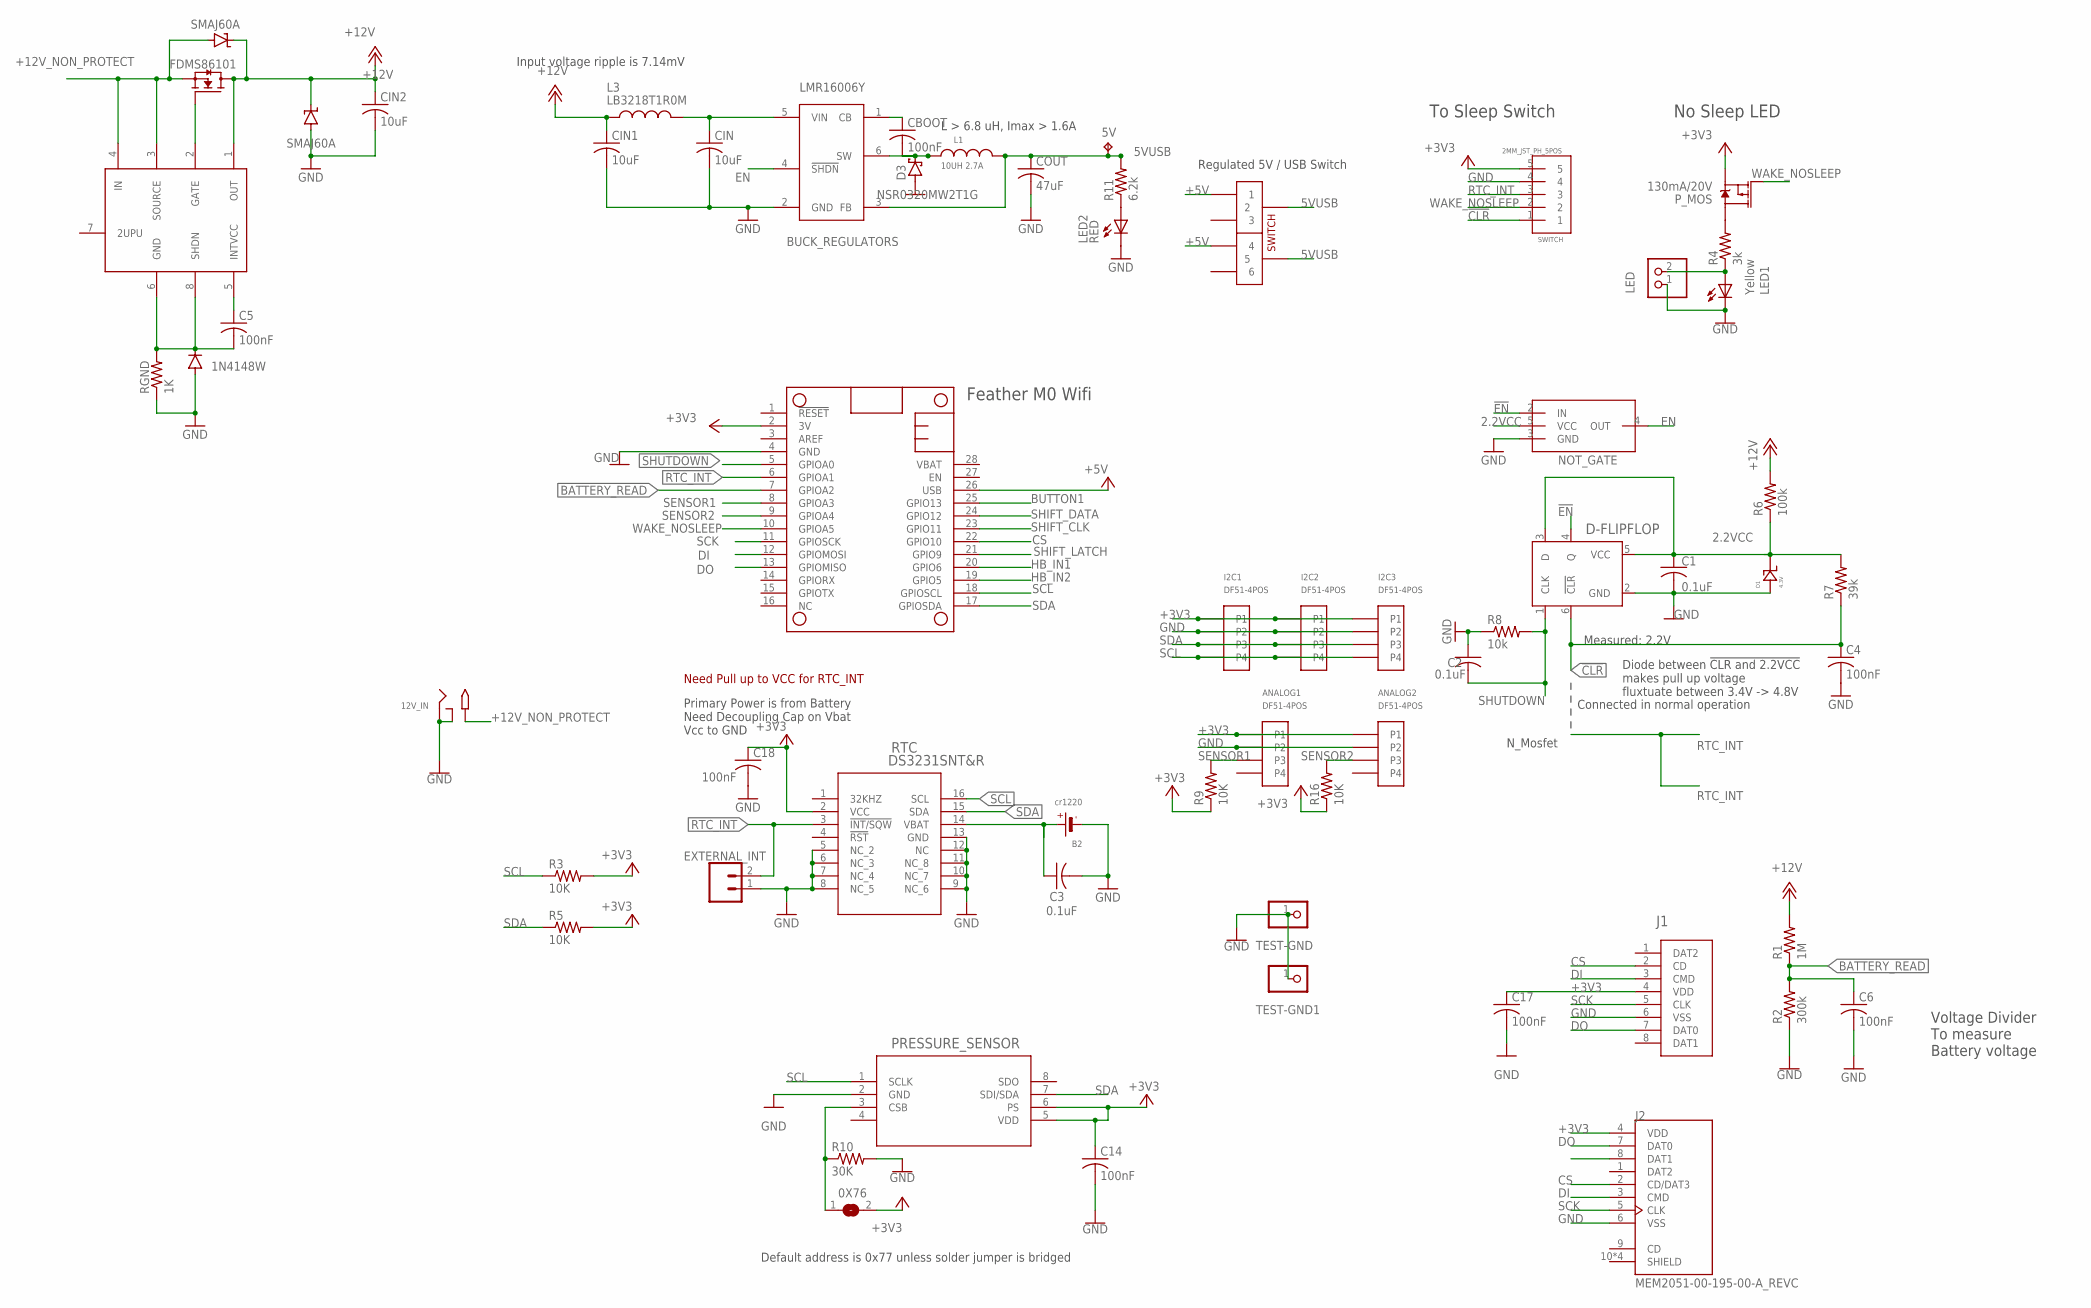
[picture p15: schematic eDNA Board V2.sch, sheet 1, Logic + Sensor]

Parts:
0X76: SJ
5V: TPTP16R; TP16R
12V_IN: 2.1MMJACKSMT; DCJACK_2MM_SMT
ANALOG1, ANALOG2: DF51-4POS
B2: cr1220; CR1220-2
C1, C2, C3: 0.1uF; C1206
C4, C5, C6, C14, C17, C18: 100nF; C1206
CBOOT: 100nF; C1206
CIN, CIN1, CIN2: 10uF; C1206K
COUT: 47uF; C1206
D1: 4.3V; DO-219AC
D2: 1N4148W; SOD-123_MINI-SMA
D3: NSR0320MW2T1G; SOD323_ST
D4, D5: SMAJ60A; DO_214
D-FLIPFLOP: SN74LVC1G175DBVR; DBV6
EXTERNAL_INT: CONN_021X02_NO_SILK; 1X02_NO_SILK
I2C1, I2C2, I2C3: DF51-4POS
J1: PJS008U-3000-0; CONN_PJS008U-3000-0_YAM
J2: MEM2051-00-195-00-A_REVC; GCT_MEM2051-00-195-00-A_REVC
L1: 10UH 2.7A; WE-MAPI_40XX
L3: LB3218T1R0M; INDC3218X200N
LED: 2.5MM_JST_UP_2POS; JST_2POS_2.5MM_UP
LED1: Yellow; CHIPLED_0805
LED2: RED; CHIPLED_0805
MS1: FEATHERWING
NMOS: FDMS86101; 8-POWERTDFN
PRESSURE_SENSOR: MS580302BA01-00; MS5803-02BA01
P_MOS: 130mA/20V; SOT23-3
R1: 1M; R1206
R2: 300k; R1206
R3, R5, R9, R16: 10K; R1206
R4: 3k; R1206
R6: 100k; R1206
R7: 39k; R1206
R8: 10k; R1206
R10: 30K; R1206
R11: 6.2k; RES_1206
RGND: 1K; R1206
RTC: DS3231SNT&R; 21-0042B_16
SWITCH: 2MM_JST_PH_5POS; 2MM_5POS_HEADER
TEST-GND, TEST-GND1: PINHD-1X1; 1X01
U$1: 2PDT_SWITCHJS-SMD; JS-DPDT-SMD
U$3: NOT_GATE; SOT753
U$7: LTC4372; SOP65P640X120-8N
VREG: BUCK_REGULATORS; SOT23-6

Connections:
2.2VCC: C1.1, D1.FNT, D-FLIPFLOP.3 (D), D-FLIPFLOP.5 (VCC), R6.1, R7.2, U$3.5 (VCC)
5VUSB: 5V.TP, COUT.1, L1.2, R11.2, U$1.P$2 (2), U$1.P$5 (5), VREG.3 (FB)
!CLR: C4.1, D-FLIPFLOP.6 (!CLR), R7.1, SWITCH.1
!EN: D-FLIPFLOP.4 (Q), U$3.2 (IN)
+3V3: 0X76.2, ANALOG1.P$1 (P1), ANALOG2.P$1 (P1), C14.1, C17.1, C18.1, I2C1.P$1 (P1), I2C2.P$1 (P1), I2C3.P$1 (P1), J1.4 (VDD), J2.4 (VDD), MS1.2 (3V), PRESSURE_SENSOR.5 (VDD), PRESSURE_SENSOR.6 (PS), P_MOS.2 (S), R3.2, R5.2, R9.1, R16.1, RTC.2 (VCC), SWITCH.5; also elsewhere on the board
+5V: MS1.26 (USB), U$1.P$1 (1), U$1.P$4 (4); also elsewhere on the board
+12V: CIN1.1, CIN2.1, D4.C, D5.C, L3.1, NMOS.5 (D), NMOS.6 (D), NMOS.7 (D), NMOS.8 (D), NMOS.9 (D), R1.2, R6.2, U$7.1 (OUT); also elsewhere on the board
+12V_NON_PROTECT: 12V_IN.PWR2 (TIP), D5.A, NMOS.1 (S), NMOS.2 (S), NMOS.3 (S), U$7.3 (SOURCE), U$7.4 (IN)
BATTERY_READ: C6.1, MS1.7 (GPIOA2), R1.1, R2.2
BUTTON1: MS1.25 (GPIO13)
CS: J1.2 (CD), J2.2 (CD/DAT3), MS1.22 (GPIO10)
DI: J1.3 (CMD), J2.3 (CMD), MS1.12 (GPIOMOSI)
DO: J1.7 (DAT0), J2.7 (DAT0), MS1.13 (GPIOMISO)
EN: U$3.4 (OUT), VREG.4 (!SHDN)
GND: 12V_IN.GND (RING), 12V_IN.GNDBREAK (RING_SW), ANALOG1.P$2 (P2), ANALOG2.P$2 (P2), B2.-, C1.2, C2.1, C3.2, C4.2, C6.2, C14.2, C17.2, C18.2, CIN.2, CIN1.2, CIN2.2, COUT.2, D1.BCK, D2.A, D3.A, D4.A, D-FLIPFLOP.2 (GND), EXTERNAL_INT.1, I2C1.P$2 (P2), I2C2.P$2 (P2), I2C3.P$2 (P2), J1.6 (VSS), J2.6 (VSS), LED.1, LED1.C, LED2.C, MS1.4 (GND), PRESSURE_SENSOR.2 (GND), R2.1, R8.1, R10.2, RGND.1, RTC.5 (NC_2), RTC.6 (NC_3), RTC.7 (NC_4), RTC.8 (NC_5), RTC.9 (NC_6), RTC.10 (NC_7), RTC.11 (NC_8), RTC.12 (NC), RTC.13 (GND), SWITCH.4, TEST-GND.1, TEST-GND1.1, U$3.3 (GND), VREG.2 (GND); also elsewhere on the board
HB_IN1: MS1.20 (GPIO6); also elsewhere on the board
HB_IN2: MS1.19 (GPIO5); also elsewhere on the board
unnamed: B2.+, C3.1, RTC.14 (VBAT)
unnamed: P_MOS.3 (D), R4.2
unnamed: LED.2, LED1.A, R4.1
unnamed: 0X76.1, PRESSURE_SENSOR.3 (CSB), R10.1
unnamed: NMOS.4 (G), U$7.2 (GATE)
unnamed: LED2.A, R11.1
unnamed: CIN.1, L3.2, VREG.5 (VIN)
unnamed: CBOOT.1, VREG.1 (CB)
unnamed: CBOOT.2, D3.C, L1.1, VREG.6 (SW)
unnamed: C5.1, U$7.5 (INTVCC)
unnamed: C5.2, D2.C, RGND.2, U$7.6 (GND), U$7.8 (SHDN)
RTC_INT: EXTERNAL_INT.2, MS1.6 (GPIOA1), RTC.3 (!INT/SQW), SWITCH.3
SCK: J1.5 (CLK), J2.5 (CLK), MS1.11 (GPIOSCK)
SCL: I2C1.P$4 (P4), I2C2.P$4 (P4), I2C3.P$4 (P4), MS1.18 (GPIOSCL), PRESSURE_SENSOR.1 (SCLK), R3.1, RTC.16 (SCL)
SDA: I2C1.P$3 (P3), I2C2.P$3 (P3), I2C3.P$3 (P3), MS1.17 (GPIOSDA), PRESSURE_SENSOR.7 (SDI/SDA), R5.1, RTC.15 (SDA)
SENSOR1: ANALOG1.P$3 (P3), MS1.8 (GPIOA3), R9.2
SENSOR2: ANALOG2.P$3 (P3), MS1.9 (GPIOA4), R16.2
SHIFT_CLK: MS1.23 (GPIO11); also elsewhere on the board
SHIFT_DATA: MS1.24 (GPIO12); also elsewhere on the board
SHIFT_LATCH: MS1.21 (GPIO9); also elsewhere on the board
SHUTDOWN: C2.2, D-FLIPFLOP.1 (CLK), MS1.5 (GPIOA0), R8.2
WAKE_NOSLEEP: MS1.10 (GPIOA5), P_MOS.1 (G), SWITCH.2

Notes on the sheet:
No Sleep LED
Feather M0 Wifi
To Sleep Switch
Voltage Divider To measure Battery voltage
Primary Power is from Battery Need Decoupling Cap on Vbat Vcc to GND
Measured: 2.2V
Connected in normal operation
N_Mosfet
Diode between !CLR and 2.2VCC makes pull up voltage fluxtuate between 3.4V -> 4.8V
Need Pull up to VCC for RTC_INT
Input voltage ripple is 7.14mV
L > 6.8 uH, Imax > 1.6A
Regulated 5V / USB Switch
Default address is 0x77 unless solder jumper is bridged

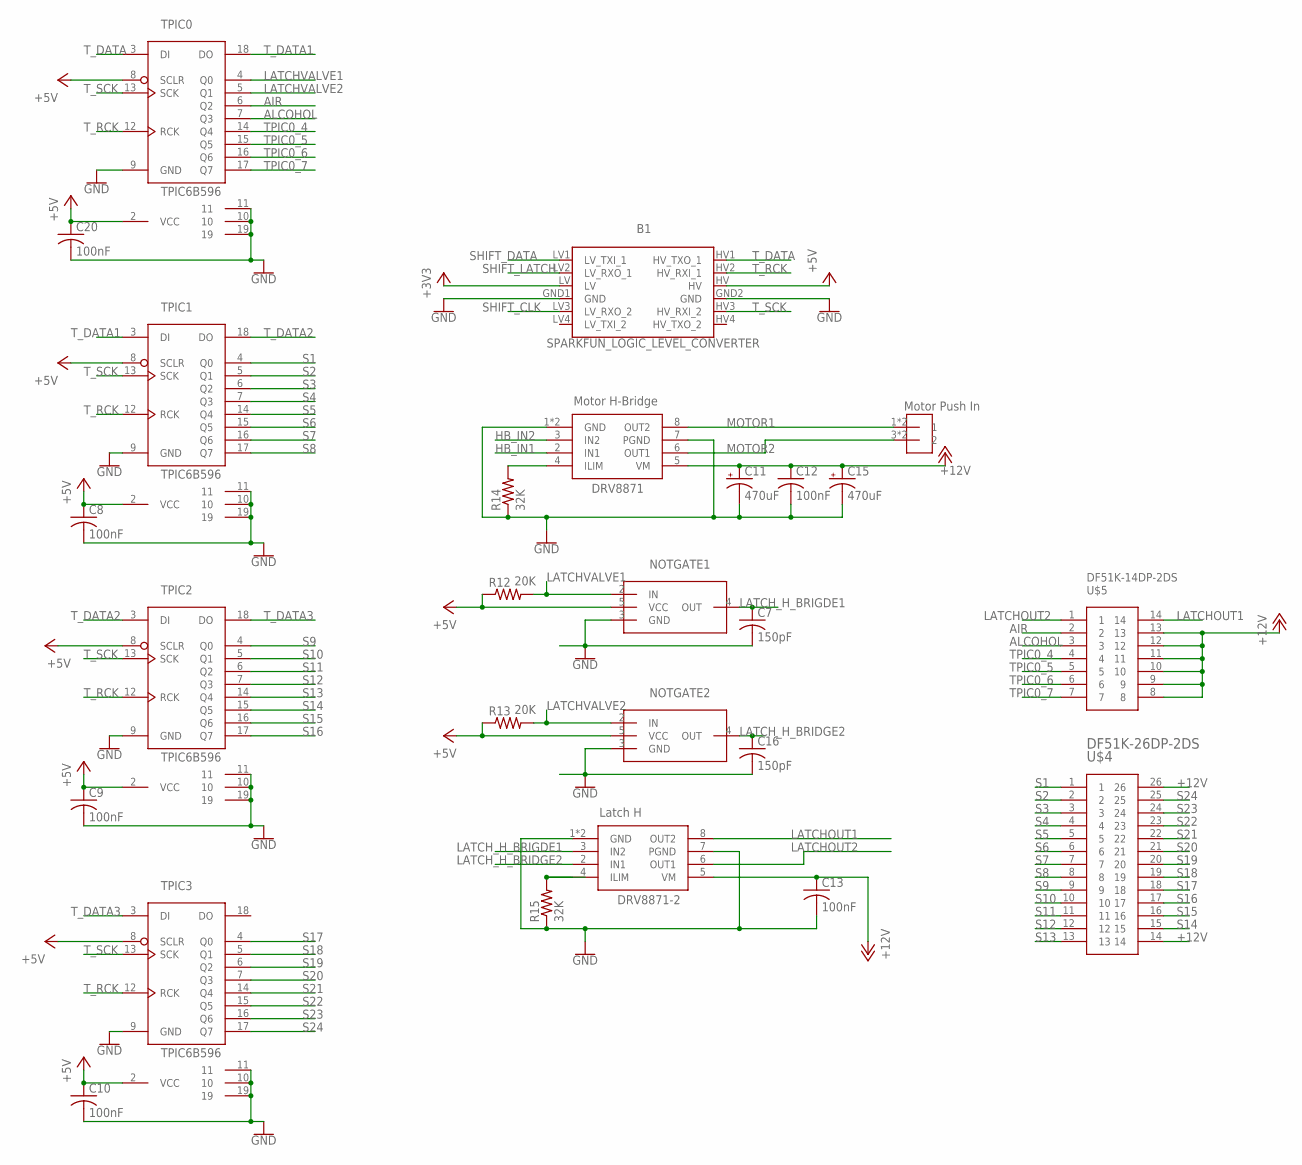
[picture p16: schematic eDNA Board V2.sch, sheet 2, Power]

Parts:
B1: SPARKFUN_LOGIC_LEVEL_CONVERTER
C7, C16: 150pF; C1206
C8, C9, C10, C12, C13, C20: 100nF; C1206
C11, C15: 470uF; 140CLH-0810
DRV8871: Motor H-Bridge; SOP8
DRV8871-2: Latch H; SOP8
NOTGATE1, NOTGATE2: NOT_GATE; SOT753
R12, R13: 20K; R1206
R14, R15: 32K; R1206
TPIC0, TPIC1, TPIC2, TPIC3: TPIC6B596; DIP20
U$2: Motor Push In; 3.5MM_DIP2
U$4: DF51K-26DP-2DS; DF51K-26DP-2DS-ANGLE
U$5: DF51K-14DP-2DS; DF51K-14DP-2DS-ANGLE

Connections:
+3V3: B1.LV; also elsewhere on the board
+5V: B1.HV, C8.1, C9.1, C10.1, C20.1, NOTGATE1.5 (VCC), NOTGATE2.5 (VCC), R12.1, R13.1, TPIC0.2 (VCC), TPIC0.8 (SCLR), TPIC1.2 (VCC), TPIC1.8 (SCLR), TPIC2.2 (VCC), TPIC2.8 (SCLR), TPIC3.2 (VCC), TPIC3.8 (SCLR); also elsewhere on the board
+12V: C11.+, C12.1, C13.1, C15.+, DRV8871.5 (VM), DRV8871-2.5 (VM), U$4.14, U$4.26, U$5.8, U$5.9, U$5.10, U$5.11, U$5.12, U$5.13; also elsewhere on the board
AIR: TPIC0.6 (Q2), U$5.2
ALCOHOL: TPIC0.7 (Q3), U$5.3
GND: B1.GND1 (GND), B1.GND2 (GND), C7.2, C8.2, C9.2, C10.2, C11.-, C12.2, C13.2, C15.-, C16.2, C20.2, DRV8871.1 (GND), DRV8871.7 (PGND), DRV8871.GND, DRV8871-2.1 (GND), DRV8871-2.7 (PGND), DRV8871-2.GND, NOTGATE1.3 (GND), NOTGATE2.3 (GND), R14.1, R15.1, TPIC0.9 (GND), TPIC0.10, TPIC0.11, TPIC0.19, TPIC1.9 (GND), TPIC1.10, TPIC1.11, TPIC1.19, TPIC2.9 (GND), TPIC2.10, TPIC2.11, TPIC2.19, TPIC3.9 (GND), TPIC3.10, TPIC3.11, TPIC3.19; also elsewhere on the board
HB_IN1: DRV8871.2 (IN1); also elsewhere on the board
HB_IN2: DRV8871.3 (IN2); also elsewhere on the board
LATCHOUT1: DRV8871-2.8 (OUT2), U$5.14
LATCHOUT2: DRV8871-2.6 (OUT1), U$5.1
LATCHVALVE1: NOTGATE1.2 (IN), R12.2, TPIC0.4 (Q0)
LATCHVALVE2: NOTGATE2.2 (IN), R13.2, TPIC0.5 (Q1)
LATCH_H_BRIDGE2: C16.1, DRV8871-2.2 (IN1), NOTGATE2.4 (OUT)
LATCH_H_BRIGDE1: C7.1, DRV8871-2.3 (IN2), NOTGATE1.4 (OUT)
MOTOR1: DRV8871.8 (OUT2), U$2.1, U$2.2 (1)
MOTOR2: DRV8871.6 (OUT1), U$2.3 (2), U$2.4 (2)
unnamed: DRV8871.4 (ILIM), R14.2
unnamed: DRV8871-2.4 (ILIM), R15.2
S1: TPIC1.4 (Q0), U$4.1
S2: TPIC1.5 (Q1), U$4.2
S3: TPIC1.6 (Q2), U$4.3
S4: TPIC1.7 (Q3), U$4.4
S5: TPIC1.14 (Q4), U$4.5
S6: TPIC1.15 (Q5), U$4.6
S7: TPIC1.16 (Q6), U$4.7
S8: TPIC1.17 (Q7), U$4.8
S9: TPIC2.4 (Q0), U$4.9
S10: TPIC2.5 (Q1), U$4.10
S11: TPIC2.6 (Q2), U$4.11
S12: TPIC2.7 (Q3), U$4.12
S13: TPIC2.14 (Q4), U$4.13
S14: TPIC2.15 (Q5), U$4.15
S15: TPIC2.16 (Q6), U$4.16
S16: TPIC2.17 (Q7), U$4.17
S17: TPIC3.4 (Q0), U$4.18
S18: TPIC3.5 (Q1), U$4.19
S19: TPIC3.6 (Q2), U$4.20
S20: TPIC3.7 (Q3), U$4.21
S21: TPIC3.14 (Q4), U$4.22
S22: TPIC3.15 (Q5), U$4.23
S23: TPIC3.16 (Q6), U$4.24
S24: TPIC3.17 (Q7), U$4.25
SHIFT_CLK: B1.LV3 (LV_RXO_2); also elsewhere on the board
SHIFT_DATA: B1.LV1 (LV_TXI_1); also elsewhere on the board
SHIFT_LATCH: B1.LV2 (LV_RXO_1); also elsewhere on the board
TPIC0_4: TPIC0.14 (Q4), U$5.4
TPIC0_5: TPIC0.15 (Q5), U$5.5
TPIC0_6: TPIC0.16 (Q6), U$5.6
TPIC0_7: TPIC0.17 (Q7), U$5.7
T_DATA: B1.HV1 (HV_TXO_1), TPIC0.3 (DI)
T_DATA1: TPIC0.18 (DO), TPIC1.3 (DI)
T_DATA2: TPIC1.18 (DO), TPIC2.3 (DI)
T_DATA3: TPIC2.18 (DO), TPIC3.3 (DI)
T_RCK: B1.HV2 (HV_RXI_1), TPIC0.12 (RCK), TPIC1.12 (RCK), TPIC2.12 (RCK), TPIC3.12 (RCK)
T_SCK: B1.HV3 (HV_RXI_2), TPIC0.13 (SCK), TPIC1.13 (SCK), TPIC2.13 (SCK), TPIC3.13 (SCK)

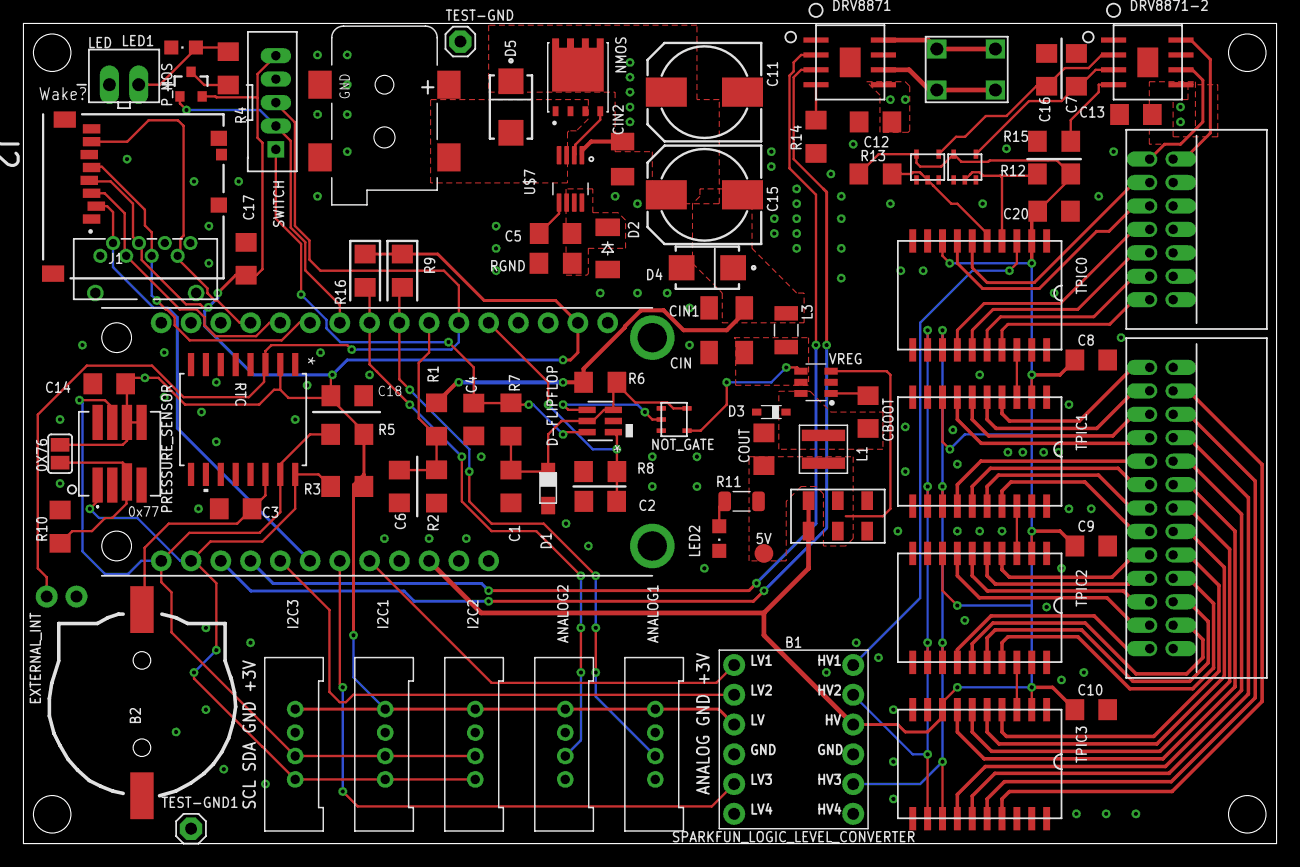
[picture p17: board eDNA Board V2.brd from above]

Board: 2 copper layers, 107.0 x 70.0 mm, 88 parts (0 on the bottom side), 84 nets.

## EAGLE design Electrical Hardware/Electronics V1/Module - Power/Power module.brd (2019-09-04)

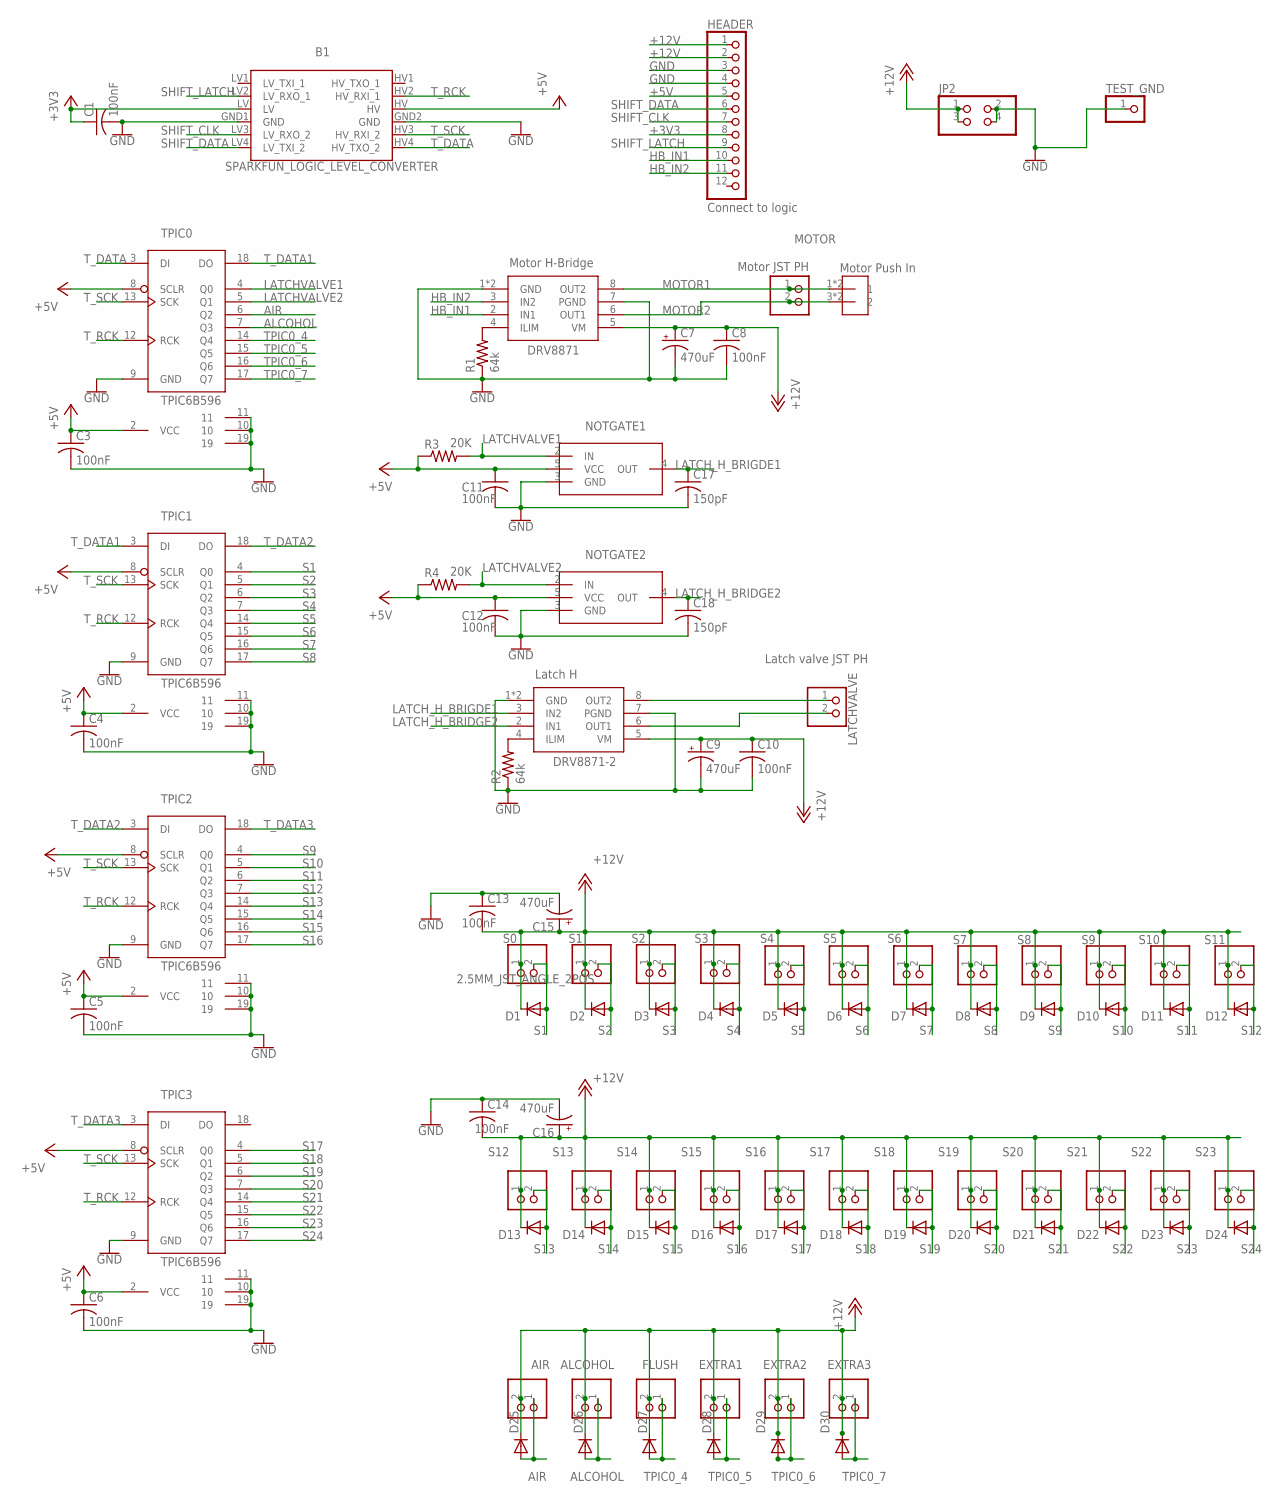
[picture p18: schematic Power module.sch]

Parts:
AIR: 2.5MM_JST_UP_2POS; JST_2POS_2.5MM_UP
ALCOHOL: 2.5MM_JST_UP_2POS; JST_2POS_2.5MM_UP
B1: SPARKFUN_LOGIC_LEVEL_CONVERTER
C1, C3, C4, C5, C6, C8, C10, C13, C14: 100nF; C050-024X044
C7, C9, C15, C16: 470uF; 140CLH-0810
C11, C12: 100nF; C1206
C17, C18: 150pF; C050-024X044
D1, D2, D3, D4, D5, D6, D7, D8, D9, D10, D11, D12, D13, D14, D15, D16, D17, D18, D19, D20, D21, D22, D23, D24, D25, D26, D27, D28, D29, D30: DIODESOD-123; SOD-123
DRV8871: Motor H-Bridge; SOP8
DRV8871-2: Latch H; SOP8
EXTRA1, EXTRA2, EXTRA3: 2.5MM_JST_UP_2POS; JST_2POS_2.5MM_UP
FLUSH: 2.5MM_JST_UP_2POS; JST_2POS_2.5MM_UP
HEADER: Connect to logic; 1X12
JP2: PINHD-2X2; 2X02
LATCHVALVE: Latch valve JST PH; JST_2POS_2.5MM_UP
MOTOR: Motor JST PH; JST_2POS_2.5MM_UP
NOTGATE1, NOTGATE2: NOT_GATE; SOT753
R1, R2: 64k; 0204/5
R3, R4: 20K; R1206
S0, S1, S2, S3, S4, S5, S6, S7, S8, S9, S10, S11, S12, S13, S14, S15, S16, S17, S18, S19, S20, S21, S22, S23: 2.5MM_JST_ANGLE_2POS; JST_2POS_2.5MM_ANGLE
TEST_GND: PINHD-1X1; 1X01
TPIC0, TPIC1, TPIC2, TPIC3: TPIC6B596; DIP20
U$1: Motor Push In; 3.5MM_DIP2

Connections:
+3V3: B1.LV, C1.1, HEADER.8
+5V: B1.HV, C3.1, C4.1, C5.1, C6.1, C11.1, C12.1, HEADER.5, NOTGATE1.5 (VCC), NOTGATE2.5 (VCC), R3.1, R4.1, TPIC0.2 (VCC), TPIC0.8 (SCLR), TPIC1.2 (VCC), TPIC1.8 (SCLR), TPIC2.2 (VCC), TPIC2.8 (SCLR), TPIC3.2 (VCC), TPIC3.8 (SCLR)
+12V: AIR.2, ALCOHOL.2, C7.+, C8.1, C9.+, C10.1, C13.2, C14.2, C15.+, C16.+, D1.C, D2.C, D3.C, D4.C, D5.C, D6.C, D7.C, D8.C, D9.C, D10.C, D11.C, D12.C, D13.C, D14.C, D15.C, D16.C, D17.C, D18.C, D19.C, D20.C, D21.C, D22.C, D23.C, D24.C, D25.C, D26.C, D27.C, D28.C, D29.C, D30.C, DRV8871.5 (VM), DRV8871-2.5 (VM), EXTRA1.2, EXTRA2.2, EXTRA3.2, FLUSH.2, HEADER.1, HEADER.2, JP2.1, JP2.3, S0.1 (2), S1.1 (2), S2.1 (2), S3.1 (2), S4.1 (2), S5.1 (2), S6.1 (2), S7.1 (2), S8.1 (2), S9.1 (2), S10.1 (2), S11.1 (2), S12.1 (2), S13.1 (2), S14.1 (2), S15.1 (2), S16.1 (2), S17.1 (2), S18.1 (2), S19.1 (2), S20.1 (2), S21.1 (2), S22.1 (2), S23.1 (2)
AIR: AIR.1, D25.A, TPIC0.6 (Q2)
ALCOHOL: ALCOHOL.1, D26.A, TPIC0.7 (Q3)
GND: B1.GND1 (GND), B1.GND2 (GND), C1.2, C3.2, C4.2, C5.2, C6.2, C7.-, C8.2, C9.-, C10.2, C11.2, C12.2, C13.1, C14.1, C15.-, C16.-, C17.2, C18.2, DRV8871.1 (GND), DRV8871.7 (PGND), DRV8871.GND, DRV8871-2.1 (GND), DRV8871-2.7 (PGND), DRV8871-2.GND, HEADER.3, HEADER.4, JP2.2, JP2.4, NOTGATE1.3 (GND), NOTGATE2.3 (GND), R1.1, R2.1, TEST_GND.1, TPIC0.9 (GND), TPIC0.10, TPIC0.11, TPIC0.19, TPIC1.9 (GND), TPIC1.10, TPIC1.11, TPIC1.19, TPIC2.9 (GND), TPIC2.10, TPIC2.11, TPIC2.19, TPIC3.9 (GND), TPIC3.10, TPIC3.11, TPIC3.19
HB_IN1: DRV8871.2 (IN1), HEADER.10
HB_IN2: DRV8871.3 (IN2), HEADER.11
LATCHVALVE1: NOTGATE1.2 (IN), R3.2, TPIC0.4 (Q0)
LATCHVALVE2: NOTGATE2.2 (IN), R4.2, TPIC0.5 (Q1)
LATCH_H_BRIDGE2: C18.1, DRV8871-2.2 (IN1), NOTGATE2.4 (OUT)
LATCH_H_BRIGDE1: C17.1, DRV8871-2.3 (IN2), NOTGATE1.4 (OUT)
MOTOR1: DRV8871.8 (OUT2), MOTOR.1, U$1.1, U$1.2 (1)
MOTOR2: DRV8871.6 (OUT1), MOTOR.2, U$1.3 (2), U$1.4 (2)
unnamed: DRV8871-2.4 (ILIM), R2.2
unnamed: DRV8871.4 (ILIM), R1.2
unnamed: DRV8871-2.8 (OUT2), LATCHVALVE.1
unnamed: DRV8871-2.6 (OUT1), LATCHVALVE.2
S1: D1.A, S0.2 (1), TPIC1.4 (Q0)
S2: D2.A, S1.2 (1), TPIC1.5 (Q1)
S3: D3.A, S2.2 (1), TPIC1.6 (Q2)
S4: D4.A, S3.2 (1), TPIC1.7 (Q3)
S5: D5.A, S4.2 (1), TPIC1.14 (Q4)
S6: D6.A, S5.2 (1), TPIC1.15 (Q5)
S7: D7.A, S6.2 (1), TPIC1.16 (Q6)
S8: D8.A, S7.2 (1), TPIC1.17 (Q7)
S9: D9.A, S8.2 (1), TPIC2.4 (Q0)
S10: D10.A, S9.2 (1), TPIC2.5 (Q1)
S11: D11.A, S10.2 (1), TPIC2.6 (Q2)
S12: D12.A, S11.2 (1), TPIC2.7 (Q3)
S13: D13.A, S12.2 (1), TPIC2.14 (Q4)
S14: D14.A, S13.2 (1), TPIC2.15 (Q5)
S15: D15.A, S14.2 (1), TPIC2.16 (Q6)
S16: D16.A, S15.2 (1), TPIC2.17 (Q7)
S17: D17.A, S16.2 (1), TPIC3.4 (Q0)
S18: D18.A, S17.2 (1), TPIC3.5 (Q1)
S19: D19.A, S18.2 (1), TPIC3.6 (Q2)
S20: D20.A, S19.2 (1), TPIC3.7 (Q3)
S21: D21.A, S20.2 (1), TPIC3.14 (Q4)
S22: D22.A, S21.2 (1), TPIC3.15 (Q5)
S23: D23.A, S22.2 (1), TPIC3.16 (Q6)
S24: D24.A, S23.2 (1), TPIC3.17 (Q7)
SHIFT_CLK: B1.LV3 (LV_RXO_2), HEADER.7
SHIFT_DATA: B1.LV4 (LV_TXI_2), HEADER.6
SHIFT_LATCH: B1.LV2 (LV_RXO_1), HEADER.9
TPIC0_4: D27.A, FLUSH.1, TPIC0.14 (Q4)
TPIC0_5: D28.A, EXTRA1.1, TPIC0.15 (Q5)
TPIC0_6: D29.A, EXTRA2.1, TPIC0.16 (Q6)
TPIC0_7: D30.A, EXTRA3.1, TPIC0.17 (Q7)
T_DATA: B1.HV4 (HV_TXO_2), TPIC0.3 (DI)
T_DATA1: TPIC0.18 (DO), TPIC1.3 (DI)
T_DATA2: TPIC1.18 (DO), TPIC2.3 (DI)
T_DATA3: TPIC2.18 (DO), TPIC3.3 (DI)
T_RCK: B1.HV2 (HV_RXI_1), TPIC0.12 (RCK), TPIC1.12 (RCK), TPIC2.12 (RCK), TPIC3.12 (RCK)
T_SCK: B1.HV3 (HV_RXI_2), TPIC0.13 (SCK), TPIC1.13 (SCK), TPIC2.13 (SCK), TPIC3.13 (SCK)

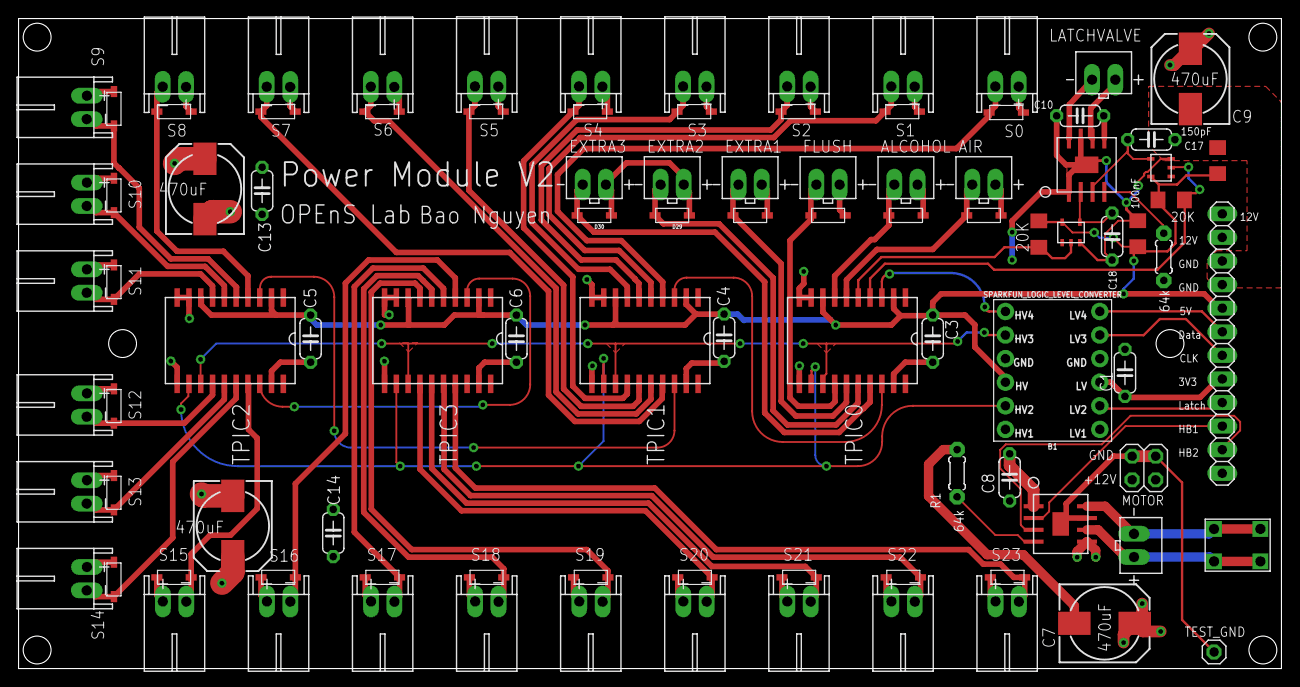
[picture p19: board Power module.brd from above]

Board: 2 copper layers, 136.0 x 70.0 mm, 96 parts (0 on the bottom side), 55 nets.

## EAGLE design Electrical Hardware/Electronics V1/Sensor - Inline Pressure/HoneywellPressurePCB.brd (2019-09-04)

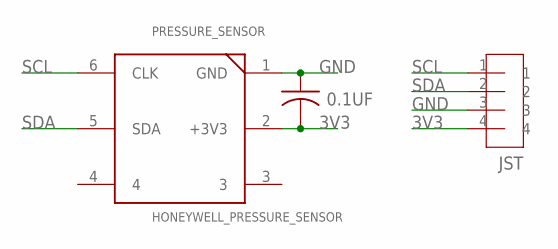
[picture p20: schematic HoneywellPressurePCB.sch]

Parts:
0.1UF: C-USC1206; C1206
JST: 2.5MM_JST_UP_4POS; JST_4POS_2.5MM_UP
PRESSURE_SENSOR: HONEYWELL_PRESSURE_SENSOR; DIP6

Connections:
3V3: 0.1UF.2, JST.4, PRESSURE_SENSOR.2 (+3V3)
GND: 0.1UF.1, JST.3, PRESSURE_SENSOR.1 (GND)
SCL: JST.1, PRESSURE_SENSOR.6 (CLK)
SDA: JST.2, PRESSURE_SENSOR.5 (SDA)

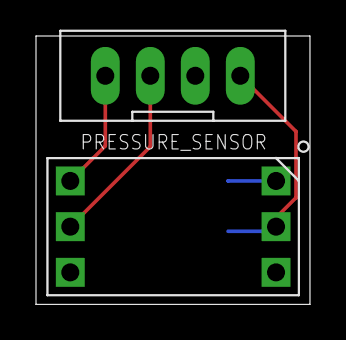
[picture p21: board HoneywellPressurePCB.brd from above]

Board: 2 copper layers, 15.2 x 14.9 mm, 3 parts (1 on the bottom side), 4 nets.

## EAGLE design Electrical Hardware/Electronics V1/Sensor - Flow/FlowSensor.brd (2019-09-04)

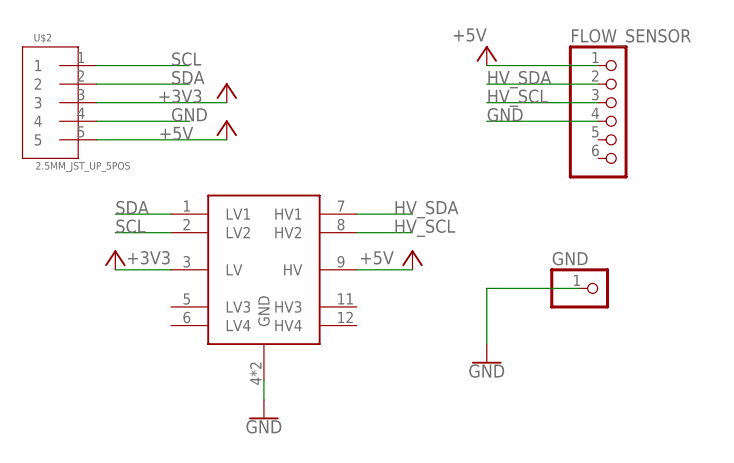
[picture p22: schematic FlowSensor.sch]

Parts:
FLOW_SENSOR: PINHD-1X6; 1X06
GND: PINHD-1X1; 1X01
U$1: LOGIC_LEVEL_CONVERTER
U$2: 2.5MM_JST_UP_5POS; JST_5POS_2.5MM_UP

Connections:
+3V3: U$1.3 (LV), U$2.3
+5V: FLOW_SENSOR.1, U$1.9 (HV), U$2.5
GND: FLOW_SENSOR.4, GND.1, U$1.4 (GND), U$1.10 (GND), U$2.4
HV_SCL: FLOW_SENSOR.3, U$1.8 (HV2)
HV_SDA: FLOW_SENSOR.2, U$1.7 (HV1)
SCL: U$1.2 (LV2), U$2.1
SDA: U$1.1 (LV1), U$2.2

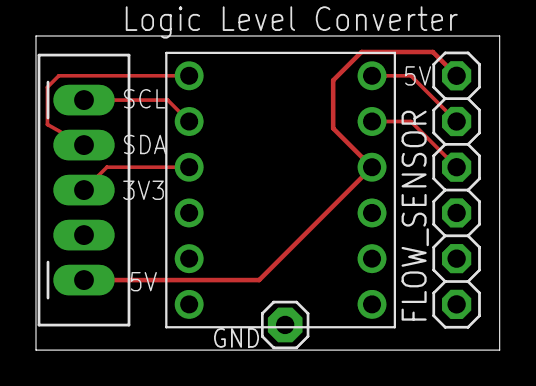
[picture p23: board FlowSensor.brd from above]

Board: 2 copper layers, 25.8 x 17.4 mm, 4 parts (0 on the bottom side), 7 nets.

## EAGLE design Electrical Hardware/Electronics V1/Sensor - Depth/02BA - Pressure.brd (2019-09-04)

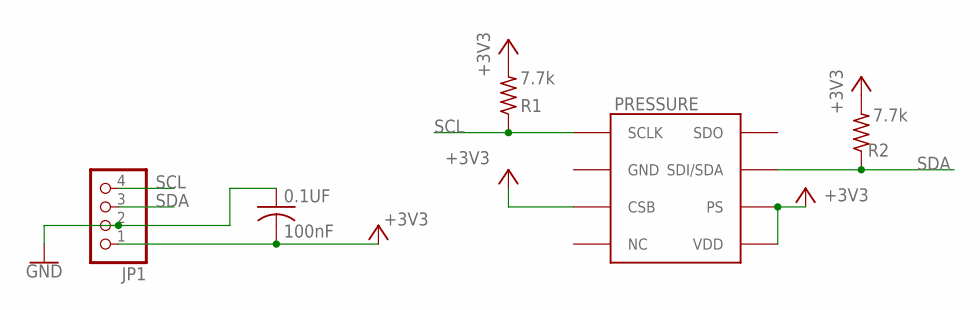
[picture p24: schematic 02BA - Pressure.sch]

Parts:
0.1UF: 100nF; C0805
JP1: PINHD-1X4; 1X04
PRESSURE: MS5803-01BA; SMD
R1, R2: 7.7k; R0805

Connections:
+3V3: 0.1UF.2, JP1.1, PRESSURE.CSB, PRESSURE.PS, PRESSURE.VDD, R1.2, R2.2
GND: 0.1UF.1, JP1.2
SCL: JP1.4, PRESSURE.SCLK, R1.1
SDA: JP1.3, PRESSURE.SDI/SDA, R2.1

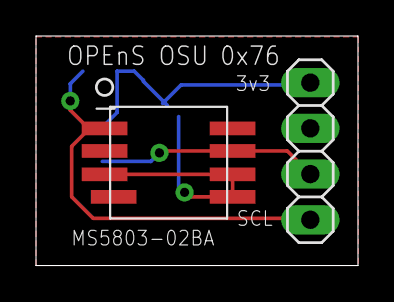
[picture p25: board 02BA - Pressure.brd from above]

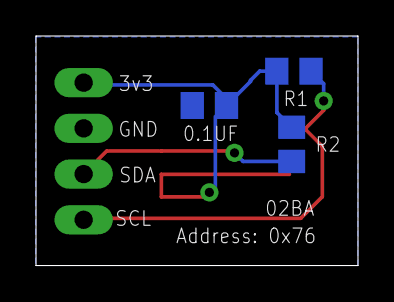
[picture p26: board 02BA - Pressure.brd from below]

Board: 2 copper layers, 17.9 x 12.8 mm, 5 parts (3 on the bottom side), 4 nets.

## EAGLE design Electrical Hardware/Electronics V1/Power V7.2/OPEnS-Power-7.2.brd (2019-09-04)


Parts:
12V_IN: 2.1MMJACKSMT; DCJACK_2MM_SMT
B_CELL: CR1220SMT; CR1220-SMD
C1, C2, C3, C4: 0.1uF; C1206
C12: 470 uF; 153CLV-0810
C13: 100uF; 153CLV-0505
D1: 4.3V; DO-219AC
D2, D4: S1A-13-F; SMA
D3: RED; LED-1206
D-FLIPFLOP: SN74LVC1G175DBVR; DBV6
J2: CONN_05; 1X05
JP1: PINHD-1X7; 1X07
JP2: PINHD-1X1; 1X01
L1: L471; 12-12
MODE: PINHD-1X3; 1X03
MOSFET: MOSFET-SOT23F; SOT-23F
R1: 128k; R1206
R2: 30k; R1206
R3, R4: 10k; R1206
R5: 300k; R1206
R6: 1k-3k; R1206
U2: DS3231SNT&R; 21-0042B_16
U3: LM2575SX-5.0/NOPB; KTT0005B

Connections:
5_RAW: C12.+, D3.A, L1.B, MODE.1, U3.4 (FB)
!CLR: D2.1, D-FLIPFLOP.6 (!CLR), J2.5
+5V: J2.3, MODE.2
+12V: 12V_IN.PWR2 (TIP), C13.+, JP1.5, R1.2, U3.1 (VIN)
EN_: D-FLIPFLOP.4 (Q), JP1.1, U3.5 (STATE)
GND: 12V_IN.GND (RING), 12V_IN.GNDBREAK (RING_SW), B_CELL.-, C1.2, C2.1, C3.2, C4.2, C12.-, C13.-, D1.BCK, D4.2, D-FLIPFLOP.2 (GND), JP1.7, JP2.1, MOSFET.S, R3.1, R4.1, R6.1, U2.2 (VCC), U2.5 (NC_2), U2.6 (NC_3), U2.7 (NC_4), U2.8 (NC_5), U2.9 (NC_6), U2.10 (NC_7), U2.11 (NC_8), U2.12 (NC), U2.13 (GND), U3.3 (GND), U3.6 (PAD)
INT_2: J2.4, MOSFET.G, R4.2
unnamed: D4.1, L1.A, U3.2 (OUT)
unnamed: C1.1, D1.FNT, D-FLIPFLOP.3 (D), D-FLIPFLOP.5 (VCC), R1.1, R2.2
unnamed: B_CELL.+$1 (+), B_CELL.+$2 (+1), C3.1, U2.14 (VBAT)
unnamed: D2.2, R2.1
unnamed: D3.C, R6.2
RTC_INT: C4.1, JP1.4, MOSFET.D, R5.2, U2.3 (!INT/SQW)
RTC_READ: JP1.2, R5.1
SCL: J2.1, U2.16 (SCL)
SDA: J2.2, U2.15 (SDA)
SHUTDOWN: C2.2, D-FLIPFLOP.1 (CLK), JP1.3, R3.2

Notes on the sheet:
Measured: 1.9V
Primary Power is from Battery Need Decoupling Cap on Vbat Vcc to GND
Connected in normal operation
N_Mosfet
Voltage measured at VCC of Flipflop during normal operation (2.2V) and override (2.0V) Current draw at idle normal operation (6.32mA) and override (6.32mA)
R5 must be much larger than R2 Pull up power need to be larger than floating RTC_READ when the Feather is as sleep



Board: 2 copper layers, 25.0 x 54.0 mm, 27 parts (5 on the bottom side), 17 nets.

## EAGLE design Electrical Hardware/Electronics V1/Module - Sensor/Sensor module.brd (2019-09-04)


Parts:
0X76: SJ
ANALOG1, ANALOG2: AUDIOJACK_2.5MM_SMD; AJ_2.5_SMD
C1: 100nF; C1206
FLOW_SENSOR: 2.5MM_JST_UP_5POS; JST_5POS_2.5MM_UP
I2C_1: PINHD-2X4; 2X04
JP3, JP4: PINHD-2X4; 2X04
POWER: 2.5MM_JST_UP_2POS; JST_2POS_2.5MM_UP
POWER_3-5: PINHD-2X4; 2X04
PRESSURE_SENSOR: MS580302BA01-00; MS5803-02BA01
R1, R2, R3, R4, R9, R10: 30K; R1206
R5, R6: R-US_R1206; R1206
R7, R8: 10K; 0204/7
S1: Button; TACTILE_SWITCH_PTH_6.0MM
SCL_SDA: 2.5MM_JST_UP_2POS; JST_2POS_2.5MM_UP
TEST_GND: PINHD-1X1; 1X01
TO_LOGIC_BOARD1, TO_LOGIC_BOARD2: PINHD-1X6CB; 1X06-CLEANBIG
U$1, U$2, U$5: I2C; AJ_2.5_SMD

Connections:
+3V3: 0X76.2, C1.1, FLOW_SENSOR.3, I2C_1.5, I2C_1.6, JP3.7, JP4.7, POWER.1, POWER_3-5.6, POWER_3-5.8, PRESSURE_SENSOR.5 (VDD), PRESSURE_SENSOR.6 (PS), R5.2, R6.2, R7.2, R8.2, R9.2, TO_LOGIC_BOARD1.4, U$1.4, U$2.4, U$5.4
+5V: FLOW_SENSOR.1, POWER_3-5.2, POWER_3-5.4, TO_LOGIC_BOARD2.1
BUTTON1: R9.1, S1.1, TO_LOGIC_BOARD2.2
GND: ANALOG1.1, ANALOG2.1, C1.2, FLOW_SENSOR.2, I2C_1.7, I2C_1.8, POWER.2, POWER_3-5.1, POWER_3-5.3, POWER_3-5.5, POWER_3-5.7, PRESSURE_SENSOR.2 (GND), R1.1, R4.2, R10.2, S1.3 (2), TEST_GND.1, TO_LOGIC_BOARD2.6, U$1.1, U$2.1, U$5.1
unnamed: 0X76.1, PRESSURE_SENSOR.3 (CSB), R10.1
unnamed: ANALOG1.4, JP3.6, JP3.8, R2.1
unnamed: JP3.3, R2.2
unnamed: JP3.1, R1.2
unnamed: JP4.3, R3.2
unnamed: ANALOG2.4, JP4.6, JP4.8, R3.1
unnamed: JP4.1, R4.1
SCL: FLOW_SENSOR.5, I2C_1.1, I2C_1.2, PRESSURE_SENSOR.1 (SCLK), R5.1, R8.1, SCL_SDA.1, TO_LOGIC_BOARD1.1, U$1.3, U$2.3, U$5.3
SDA: FLOW_SENSOR.4, I2C_1.3, I2C_1.4, PRESSURE_SENSOR.7 (SDI/SDA), R6.1, R7.1, SCL_SDA.2, TO_LOGIC_BOARD1.2, U$1.2, U$2.2, U$5.2
SENSOR1: ANALOG1.2, JP3.2, JP3.4, TO_LOGIC_BOARD1.5
SENSOR2: ANALOG2.2, JP4.2, JP4.4, TO_LOGIC_BOARD1.6

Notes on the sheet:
I2C
Analog
Button
Default address is 0x77 unless solder jumper is bridged


Board: 2 copper layers, 40.0 x 70.0 mm, 29 parts (0 on the bottom side), 15 nets.

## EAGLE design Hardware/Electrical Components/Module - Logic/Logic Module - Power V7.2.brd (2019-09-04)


Board: 2 copper layers, 70.5 x 70.0 mm, 16 parts (1 on the bottom side), 23 nets.

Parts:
FERRITEBEAD: FB
GND_JUMPER: SMT-JUMPER_2_NO_NO-SILK
LED: 2.5MM_JST_UP_2POS; JST_2POS_2.5MM_UP
LED1: Orange; LED3MM
MS1: FEATHERWING
P_MOS: 130mA/20V; SOT23-3
R1: 1M; R1206
R2: 300k; R1206
R4: 200; 0204/7
SWITCH: 2.5MM_JST_UP_5POS; JST_5POS_2.5MM_UP
TEST-GND: 1X01
TO_POWER_BOARD: 1X12
TO_SENSOR_BOARD1, TO_SENSOR_BOARD2: 1X06-CLEANBIG
U$1: OPENS_POWER_7.2
U$2: OPENS-LOGO

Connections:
!CLR: SWITCH.1, U$1.8
+3V3: MS1.2, P_MOS.2, SWITCH.5, TO_POWER_BOARD.8, TO_SENSOR_BOARD1.4
+5V: MS1.26, TO_POWER_BOARD.5, TO_SENSOR_BOARD2.1, U$1.10
+12V: R1.2, TO_POWER_BOARD.1, TO_POWER_BOARD.2, U$1.5
BATTERY_READ: MS1.7, R1.1, R2.2
BUTTON1: MS1.25, TO_SENSOR_BOARD2.2
GND: FERRITEBEAD.P$2, GND_JUMPER.1, LED.1, LED1.K, MS1.4, R2.1, SWITCH.4, TEST-GND.1, TO_POWER_BOARD.3, TO_POWER_BOARD.4, U$1.7
HB_IN1: MS1.20, TO_POWER_BOARD.10
HB_IN2: MS1.19, TO_POWER_BOARD.11
unnamed: P_MOS.3, R4.2
unnamed: LED.2, LED1.A, R4.1
unnamed: FERRITEBEAD.P$1, GND_JUMPER.2, TO_SENSOR_BOARD2.6
RTC_INT: SWITCH.3, U$1.4
RTC_READ: MS1.6, U$1.2
SCL: MS1.18, TO_SENSOR_BOARD1.1, U$1.12
SDA: MS1.17, TO_SENSOR_BOARD1.2, U$1.11
SENSOR1: MS1.8, TO_SENSOR_BOARD1.5
SENSOR2: MS1.9, TO_SENSOR_BOARD1.6
SHIFT_CLK: MS1.23, TO_POWER_BOARD.7
SHIFT_DATA: MS1.24, TO_POWER_BOARD.6
SHIFT_LATCH: MS1.21, TO_POWER_BOARD.9
SHUTDOWN: MS1.5, U$1.3
WAKE_NOSLEEP: MS1.10, P_MOS.1, SWITCH.2

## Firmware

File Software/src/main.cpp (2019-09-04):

#include "KPLogging.hpp"
#include "KPPowerManagement.hpp"
#include "KPPump.hpp"
#include "KPSDCard.hpp"
#include "KPSensorManager.hpp"
#include "KPSerialCommand.hpp"
#include "KPServer.hpp"
#include "KPShiftRegister.hpp"
#include "KPSystemEnvironment.hpp"
#include "KPTaskManager.hpp"

#define BitCount 32

KPSDCard card;
KPPump pump("pump", Motor_Forward_Pin, Motor_Reverse_Pin);
KPShiftRegister shift(BitCount, Shift_Register_Data_Pin, Shift_Register_Clock_Pin, Shift_Register_Latch_Pin);
KPServer web("web", "eDNA", "password");
KPSerialCommand serial_command;
KPPowerManagement power;

KPSensorManager sensor_manager;
KPLogging logging_system;

//===============================================
// [+_+] Shift Register devices
//===============================================
enum ShiftDevice { Air = 2,
                   Alcohol = 3,
                   Flush = 4 };

//===============================================
// [+_+] Stop KPState
//===============================================
class StopState : public KPState {
public:
    void update(KPStateMachine & machine) override {
        KPStatus & status = KPStatus::current();
        if (timeSinceLastTransition() >= 2) {
            pump.off();
            shift.writeZeros();
            shift.writeLatchOut();

            if (status.valveCurrent <= status.valveLowerBound) {
                status.valveCurrent = status.valveLowerBound;
                status.isFull = true;
            } else {
				status.valves[status.valveCurrent] = 0;
                status.valveCurrent--;
                // power.scheduleNextAlarm(status.samplingInteval);
            }

            machine.transitionTo(KPStateIdentifier::idle);
            Serial.println(F("Transitioning to Idle"));
        }
    }
};

//===============================================
// [+_+] Decontamination KPState
//===============================================
class DecontaminateState3 : public KPState {
public:
	int count = 0;

	void update(KPStateMachine & machine) override {
		if (isInitialTransition()) {
			shift.writeZeros();
			shift.writeLatchOut();
			shift.set(Alcohol, HIGH);
			shift.set(Flush, HIGH);
			shift.flush();
			pump.on();
			count++;
		} 
		
		// Alcohol intake for 3 seconds
		if (timeSinceLastTransition() >= 3) {
			shift.set(Alcohol, LOW);
			shift.flush();
			pump.on(Direction::reverse);
		}

		// Purge the system for 12 seconds
		if (timeSinceLastTransition() >= 15) {
			if (count == 2) {
				count = 0;
				machine.transitionTo(KPStateIdentifier::stop);
			} else {
				machine.transitionTo(KPStateIdentifier::decontaminate2);
			}
		}
	}
};

class DecontaminateState2 : public KPState {
public: 
	void update(KPStateMachine & machine) override {
		if (isInitialTransition()) {
			// Turn off all the valves except the Air intake and rise the pressure until 15 psi
			shift.setZeros();
			shift.set(Air, HIGH);
			shift.flush();
			pump.on();
		}

		if (KPStatus::current().pressure >= 15) {
			pump.off();
            shift.set(Flush, HIGH);
            shift.flush();
			delay(3000);

			machine.transitionTo(KPStateIdentifier::decontaminate3);
		}
	}
};


class DecontaminateState1 : public KPState {
public:

    void update(KPStateMachine & machine) override {
        auto status = KPStatus::current();
        if (isInitialTransition()) {
            // Turn everything off
            pump.off();
            shift.writeLatchOut();
            shift.setZeros();
            shift.flush();

            // Turn on the flush valve, the air intake, and the pump to clean out the main pipe
            shift.set(Flush, HIGH);
            shift.set(Air, HIGH);
            shift.flush();
            pump.on();
        }

        // After 10 seconds, get rid of the water between the filter and the main pipe
        if (timeSinceLastTransition() >= 10) {
            // Rise the pressure in the system to 1.7 psi
            pump.pwm(0.75);
            shift.set(Flush, LOW);
            shift.flush();

            if (status.pressure >= 1.7) {
                int r = shift.registerIndex(status.valveCurrent) + 1;
                int b = shift.bitIndex(status.valveCurrent);

                pump.off();
                shift.setRegister(r, b, HIGH);
                shift.flush();
				delay(50);

				machine.transitionTo(KPStateIdentifier::decontaminate2);
            }
        }
    }
};

//===============================================
// [+_+] Preserve KPState
//===============================================
class PreserveState : public KPState {
public:
    PreserveState() {
        timeLimit = 15;
        timeMax = MinsToSecs(1);
    }

    void update(KPStateMachine & machine) override {
        if (isInitialTransition()) {
            int r = shift.registerIndex(KPStatus::current().valveCurrent) + 1;
            int b = shift.bitIndex(KPStatus::current().valveCurrent);

            shift.writeLatchOut();
            shift.setZeros();
            shift.set(Alcohol, HIGH);
            shift.setRegister(r, b, HIGH);  // Filter
            shift.flush();
            pump.on();
        }

        if (timeSinceLastTransition() >= timeLimit) {
            machine.transitionTo(KPStateIdentifier::decontaminate1);
            Serial.println(F("Transitioning to Stop"));
        }
    }
};

//===============================================
// [+_+] Clean KPState
//===============================================
class DryState : public KPState {
public:
    void update(KPStateMachine & machine) override {
        KPStatus & status = KPStatus::current();
        if (isInitialTransition()) {
            int r = shift.registerIndex(status.valveCurrent) + 1;
            int b = shift.bitIndex(status.valveCurrent);

            shift.setZeros();
            shift.set(Air, HIGH);
            shift.setRegister(r, b, HIGH);  // Filter
            shift.flush();
            pump.on();
        }

        if (timeSinceLastTransition() >= 10) {
            machine.transitionTo(KPStateIdentifier::preserve);
            Serial.println(F("Transitioning to Preserve"));
        }
    }
};

//===============================================
// [+_+] Sample KPState
//===============================================
class SampleState : public KPState {
public:
    SampleState() {
        timeLimit = MinsToSecs(3);
        timeMax = MinsToSecs(20);
        pressureLimit = 8;
        pressureMax = 15;
        volumeLimit = 1000;
        volumeMax = 5000;
    }

    void update(KPStateMachine & machine) override {
        KPStatus status = KPStatus::current();
        if (isInitialTransition()) {
            int r = shift.registerIndex(status.valveCurrent) + 1;
            int b = shift.bitIndex(status.valveCurrent);

            shift.setZeros();
            shift.writeLatchIn();
            shift.setRegister(r, b, HIGH);  // Filter
            shift.flush();
            pump.on();
        }

        // Transition to clean when the pressure exceeds 8 PSI or when exceeds 15 seconds
        if (timeSinceLastTransition() >= timeLimit || status.pressure >= pressureLimit) {
            machine.transitionTo(KPStateIdentifier::dry);
            shift.writeLatchOut();
            Serial.println(F("Transitioning to Clean"));
        }
    }
};

//===============================================
// [+_+] Flush KPState
//===============================================
class FlushState : public KPState {
public:
    FlushState() {
        timeLimit = 120;
        timeMax = MinsToSecs(7);
        volumeLimit = 1000;
        volumeMax = 5000;
    }

    void update(KPStateMachine & machine) override {
        if (isInitialTransition()) {
			shift.setZeros();				// Reset TPIC values
            shift.writeLatchIn();
            shift.set(Flush, HIGH);
            shift.flush();
			pump.on();
        }

        if (timeSinceLastTransition() >= timeLimit) {
            machine.transitionTo(KPStateIdentifier::sample);
            Serial.println(F("Transitioning to Sample"));
        }
    }
};
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

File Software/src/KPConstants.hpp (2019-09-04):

#pragma once

//===============================================================
// [+_+] Marcos
//===============================================================
#define MinsToSecs(x) 		(x * 60)
#define SecsToMillis(x) 	(x * 1000)

//===============================================================
// [+_+] Pins
//===============================================================
#define Power_Module_Pin 			A0
#define RTC_Interrupt_Pin 			A1
#define Battery_Voltage_Pin			A2
#define Analog_Sensor_1_Pin 		A3
#define Analog_Sensor_2_Pin 		A4
#define Override_Mode_Pin			A5
#define Motor_Forward_Pin			 5
#define Motor_Reverse_Pin			 6
#define Shift_Register_Latch_Pin	 9
#define SDCard_Pin 					10
#define Shift_Register_Clock_Pin	11
#define Shift_Register_Data_Pin		12
#define Button_Pin					13

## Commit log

2019-05-25 Initial Publication
    eDNA framework derived from OPEnSampler Framework including support for:
    - System-Components Design Pattern
    - Async Task Scheduling
    - State Machine
    Added Components:
    - Web Server with callback support
    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
2019-05-25 Added ArduinoSSC Library
2019-06-08 Added a bunch of functionalities
    + RTC time keeping
    + Power management
    + JSON APIs using ArduinoJSON
    + Simplified shift register APIs
    o Bug fixes
    - Action.hpp
2019-07-11 First Hardware Update
    +Add BOM, schematic, PCB for: Power Module, Logic Module, Sensor Module, Depth Sensor, Inline Pressure Sensor, Flow Sensor.
    +Add library + example code for Depth Sensor (MS5803-02BA): MS5803-02.zip
    +Add basic I2C arduino code for Flow Sensor: flowsensor.ino
    [02BA - Pressure.brd, 02BA - Pressure.sch, 3PDT Switch Breakout.brd, 3PDT Switch Breakout.sch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]
2019-07-20 Clarify text in PCBs
    O Add text for 3PDT Switch breakout board better PCB annotation
    O Rename MOSFET that controls LED for Programming Mode -> P_MOS
    + Add JST Male to BOM Logic Module – Power V8
    O Correct excel formula for a total price of Logic Module
    [3PDT Switch Breakout.brd, BOM Logic Module - Power V8.xlsx, Logic Module - Power V8.brd, Logic Module - Power V8.sch]
2019-07-20 Changing deep sleep power board to v7.2
    + Add OpenSPower V7.2: bugs fixed from version v7.1. Now stable under motor noise.
    + Add Logic Module V2 – Power V7.2: Apply new change in PCB to work with OpenSPower V7.2. The 5V voltage regulator is now in the OpenSPower board instead of on the Power Module. Switch pins are also 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
    - Remove power N-type MOSFET that controls power for Power Module V2 since power consumption in idle without MOSFET is suitable with the battery.
    [BOM Logic Module - Power V7.2.xlsx, BOM OPEnS Power 7.2.xlsx, Logic Module - Power V7.2.brd, Logic Module - Power V7.2.sch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]
2019-07-26 Major fix for sensor module
    O Power Module: Changes in footprint location of motor push-to-connect for mounting place. Move the 90-angle header further inside for better mechanical support
    O Sensor Module: Rearrange 2.5mm headphone jack closer to the edge for proper mounting. The older version stops the male jack fully dock with the female casing thus fail to connect. Move the 90-angle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
    O MS5803-02BA: Change symbol, change SDA -> SDO. This label caused the PCB to stop working with all I2C devices. Sensor Module: Rewire to the write SDA, tested.
    + Add MS5803-02BA Datasheet
    [Logic Module - Power V7.2.brd, Power module.brd, Sensor module.brd, Sensor module.sch]
2019-08-11 Bug fix for Powerboard 7.2V
    Changed R5 and R2 value to protect against RTC_READ floating when feather is as sleep.
    Added C4 capacitor to further protect against floating RTC_READ.
    [OPEnS-Power-7.2.brd, OPEnS-Power-7.2.sch]
2019-08-31 Remove OpenSPower V8
    This powerboard version did not function. Tested V7.2 is stable
    [BOM Baos_Board.xlsx, BOM Logic Module - Power V8.xlsx, Baos_Board.brd, Baos_Board.sch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]
2019-09-04 Web Interface 2.0
    New Features:
    + Integration of flow, barometric, and depth sensors
    + Much improved three-stages decontamination procedure
    + Ability to detect programming/normal operation
    Modifications:
    + Renamed classes and further simplification of the codebase
    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
2019-09-04 Updates
    Updated eDNA Eagle Library
    Update OpenSPower7.2 BOM
    Add OpenSPower 7.2 ReadMe
    Add picture for FlowSensor
    General clean up
    [BOM Logic Module - Power V7.2.xlsx, BOM OPEnS Power 7.2.xlsx, Power module.brd, Power module.sch]
2020-02-11 First draft for Logic Module V3
    Combine Power V7.3 with Logic Module
    [3PDT Switch Breakout.brd, 3PDT Switch Breakout.sch, BOM Logic Module - Power V7.2.xlsx, BOM Logic Module V3.xlsx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]
2020-02-11 Updated documentation for Logic Module V3, includes BOM, board pdf, gerber files, .sch and .brd files for Logic Module and 2PDT Switch.
    [2PDT Switch Breakout.brd, 2PDT Switch Breakout.sch, 3PDT Switch Breakout.brd, 3PDT Switch Breakout.sch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]
2020-02-11 Newest version of Logic Module V3
    [BOM Logic Module V3.xlsx, Logic Module V3.brd, Logic Module V3.sch]
2023-05-31 File/Folder Re-organization
    [02BA - Pressure.brd, 02BA - Pressure.sch, 2PDT Switch Breakout.brd, 2PDT Switch Breakout.sch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]
2023-07-21 Updated README.md
    Replaced old V2 Sampler Images with V4 Sampler Images
2024-01-03 Upload PolyWAG EDA FIles
    [eDNA Board V2.brd, eDNA Board V2.sch]
2024-01-03 Upload EDA FIles
    [3PDT Switch Breakout.brd, 3PDT Switch Breakout.sch]
2024-01-03 Upload CAD - Full Assembly
2024-01-26 Upload Current Sampler Code
    Uploaded the Sampler UI and Server code. Framework code still needs to be uploaded
2024-01-27 Upload Sampler Code
    Uploaded Sampler UI and Server Code there may be some issues with the addition of the Framework
2024-01-27 Uploaded CAD Files
    Uploaded all of the CAD files from Fusion 360
    [24+Filter+Assembly.f3z, 24x+Advantec+Filter+Assembly+CONCEPT.f3z, 25mm+M3+Frame+Screws.f3d, 7688N111_Vented+Plastic+Submersible+Cord+Grip.f3d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]
2024-01-27 Upload Sampler Code
    Uploaded Sampler UI, Server, and Framework Code
2024-12-13 Add files via upload
    eDNA bill of material
    [BOM eDNA Sampler v4.2.xlsx]

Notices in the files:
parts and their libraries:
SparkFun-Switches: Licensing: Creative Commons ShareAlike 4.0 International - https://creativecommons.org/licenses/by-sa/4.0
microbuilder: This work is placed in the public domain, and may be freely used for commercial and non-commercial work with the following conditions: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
